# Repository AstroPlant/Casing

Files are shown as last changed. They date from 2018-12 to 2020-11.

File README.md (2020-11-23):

# Casing

## Variants
There are three casing variants:

### `original/`
All CAD and other designs for the AstroPlant original casing / enclosure / top panel.
This casing design requires a large laser cutter that can fit panels larger than 130cm in length.
The other files, developed by Swiss fablab Onlfait, are more suitable for smaller laser cutters.

### `onlfait/`
All CAD and other designs for the AstroPlant Onlfait casing / enclosure / top panel.
This casing design can be used with smaller laser cutters (900x600mm).

### `LiteEd/`
All CAD and other designs for the AstroPlant Lite Edition casing / enclosure / top panel.
This casing design is a small size versión of original Maker Edition with some other improvements,
developed by Araiva (Spain) in order to save money.

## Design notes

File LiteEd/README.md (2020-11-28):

# AstroPlant Maker LITE Edition

We have recently involved in the AstroPlant Citizen Science Project. After building our first "Maker Edition (ME)" we considered to do some changes in order to save costs of materials to build the kit. This is our first version of new design called "Maker LITE Edition (MLE)".

Main features are:

- Smaller size and low-cost version
- A power-supply unit hounsing made in plywood (avoiding 3D printed power-supply unit housing)
- A DIY hydroponic kit using IKEA 365+ containers

## Files in this folder

This folder includes files to build the Lite version of Maker Edition. You should use a 6 mm plywood/multiplex or another material with same thinkness.

- Astroplant_v5.21_6mm multiplex_MLE_Laser.dxf >>> Lasercut CAD drawings
- Astroplant_v5.21_6mm multiplex_MLE_L20x10x1.5.dxf >>> Drawings to cut L-shapes
- MLE_BOM.xlsx >>> Bill of materials including screws and components to build the hydroponic kit
- AstroPlant costs ME vs MLE.xlsx >>> Estimated cost savings vs Maker Edition

## Details, features and instructions

Follow the link and find instructions, pictures, etc... including a DIY hydroponic kit

https://astroplant.gitbook.io/ap-community-projects/astroplant-maker-lite-edition

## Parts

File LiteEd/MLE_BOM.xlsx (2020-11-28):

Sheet: Screws
SCREWS AND NUTS - DETAIL |  |  |  |  |  | SCREWS AND NUTS
 |  | Screws | Units | Nuts | Units | Screws | Units | Nuts | Units
Case | Power supply housing and display mount | M4x12 | 12 | M4 | 12 | M2x10 | 6 | M2 | 6
 | Main case | M4x20 | 21 | M4 | 21 | M2,5x12 | 7 | M2,5 | 19
 | L 20x10x1,5 (sliding door and hydroponic base) | M3x10 | 12 | M3 | 12 | M2,5x20 | 4 | M3 | 30
Component | Fans | M3x20 | 6 | M3 | 6 | M3x10 | 16 | M4 | 33
 | LED | M3x10 | 4 | M3 |  | M3x20 | 10
 | RPi | M2,5x20 | 4 | M2,5 | 12 | M4x12 | 12
 | Camera | M2x10 | 4 | M2 | 4 | M4x20 | 21
 | Extension shield | M3x20 | 4 | M3 | 12
 | Lux sensor | M2x10 | 2 | M2 | 2
 | T/H sensor | M2,5x12 | 1 | M2,5 | 1
 | Display | M2,5x12 | 2 | M2,5 | 2
 | Power supply and switch | M2,5x12 | 4 | M2,5 | 4
 |  |  | 76 |  | 88 |  | 76 |  | 88
 | You can use extra nuts in RPi and Extension Shield to lift and separate these components from the wood panel

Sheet: DIY hydroponic
DIY Hydroponic kit, BOM
Component | Shop | Price | Link
Solution container | IKEA | 3.00 € | https://www.ikea.com/es/es/p/ikea-365-recipiente-rectangular-plastico-60393066/
Plant container | IKEA | 2.00 € | https://www.ikea.com/es/es/p/ikea-365-recipiente-rectangular-plastico-60359152/
Alternative plant container | IKEA | 1.50 € | https://www.ikea.com/es/es/p/ikea-365-recipiente-rectangular-plastico-40359148/
Grave cleaner | Amazon | 11.00 € | https://www.amazon.es/Sera-08550-Aspiradora-Elimina-cuidadosamente-suciedad/dp/B0013ZAEM0?__mk_es_ES=%C3%85M%C3%85%C5%BD%C3%95%C3%91
Air compressor | AliExpress | 4.00 € | https://es.aliexpress.com/item/4000354631274.html
L-Connector 8/8 mm. | AliExpress | 0.29 € | https://es.aliexpress.com/item/32996398304.html?scm_id=1007.14976.189023.0&scm-url=1007.14976.189023.0
Y-Connector 8/8/8 mm. | AliExpress | 0.33 € | https://es.aliexpress.com/item/1005001391306435.html?spm=a2g0s.9042311.0.0.324a63c0RPETpH
PVC Hose 8/10 mm. | AliExpress | 1.37 € | https://es.aliexpress.com/item/10000312761098.html?scm_id=1007.14976.189023.0&scm-url=1007.14976.189023.0
Total price |  | 23.49 €

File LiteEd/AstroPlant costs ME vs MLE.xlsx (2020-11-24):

 |  | Costs |  | Comments
 | Item (Exc. VAT) | Maker Ed. | Maker Lite Ed.
1.1 | AstroPlant kit | 400 € | 400 € | Prices for AstroPlant electrocnic kit may suffer changes, please check it
1.2 | AstroPlant kit shipping | 40 € | 40 € | To Spain
1.3 | L20x20x1,5 | 10 € | 10 €
1.4 | Laser | 117 € | 54 €
1.5 | 3D Power supply casing | 75 € |  | In MLE casing is made in plywood and laser costs included in 1.4 (I do now own a 3D Printer and I have to buy it)
1.6 | Waterfarm | 65 € |  | Include air pump
1.7 | IKEA Containers |  | 5 € | To make DIY hydroponic kit
1.8 | Air pump |  | 10 € | To make DIY hydroponic kit
1.9 | DIY Hydroponics accessories |  | 5 € | Like "T" connectors, etc... (you can find them by Aliexpress or Amazon)
 | Total | 707 € | 504 €
 | VAT (21%) | 148.47 € | 105.84 €
 | Total | 855.47 € | 609.84 €
 | Total saved cost (Incl. VAT): |  | -245.63 €

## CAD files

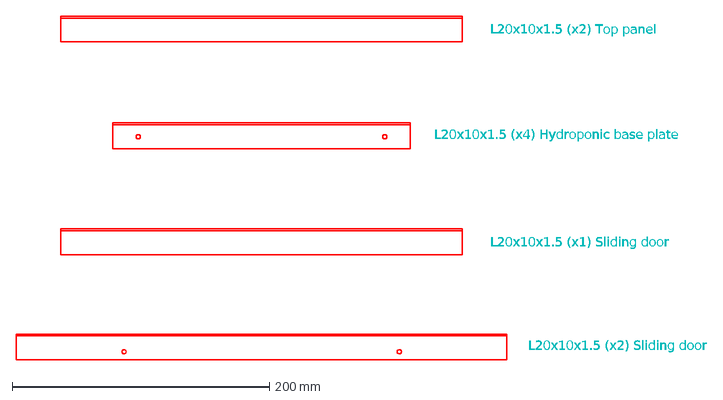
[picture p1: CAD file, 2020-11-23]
LiteEd/Astroplant_v5.21_6mm multiplex_MLE_L20x10x1.5.dxf
L20x10x1.5 (x2) Top panel
L20x10x1.5 (x4) Hydroponic base plate
L20x10x1.5 (x1) Sliding door
L20x10x1.5 (x2) Sliding door

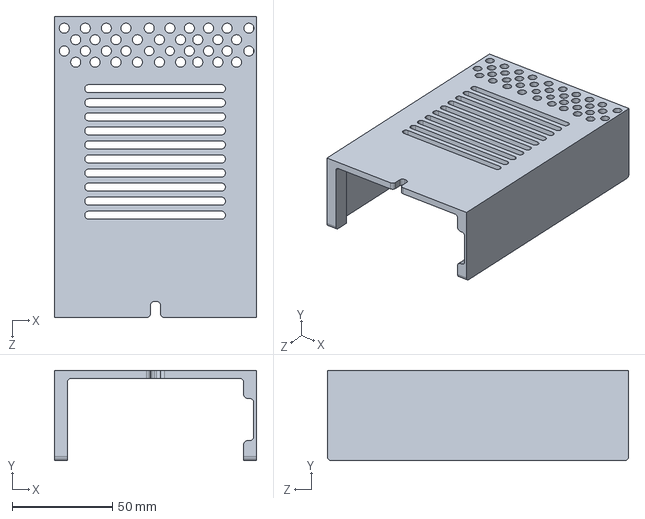
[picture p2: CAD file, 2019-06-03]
onlfait/v2.0/casingpowersupply.step
100.6 x 45.0 x 150.0 mm

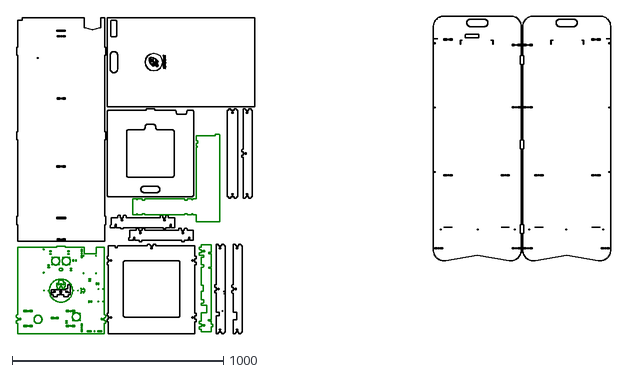
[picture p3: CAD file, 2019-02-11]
original/Laserfiles_v5.21_6mm multiplex.dxf
2812.3 x 1504.4

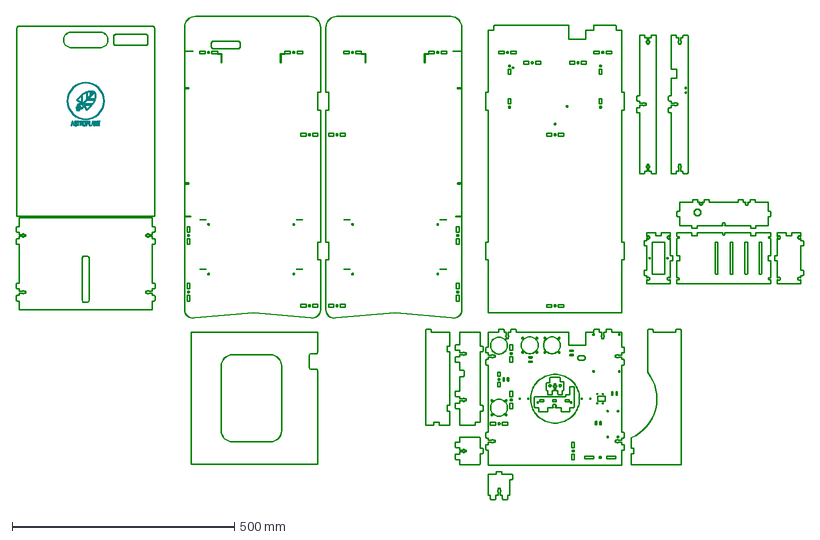
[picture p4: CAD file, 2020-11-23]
LiteEd/Astroplant_v5.21_6mm multiplex_MLE_Laser.dxf
1771.6 x 1087.4 mm

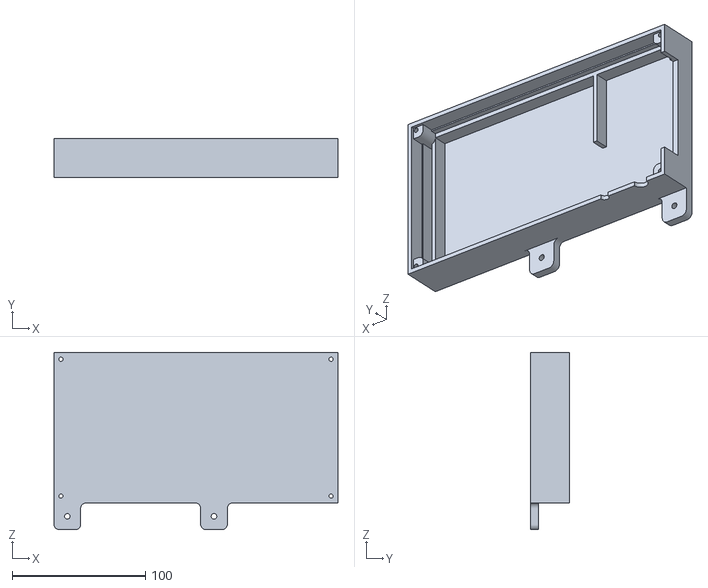
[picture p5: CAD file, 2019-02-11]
original/v5.21-Housing_powerconverter_rev02-Boss-Extrude1.STL
213.0 x 29.0 x 133.0

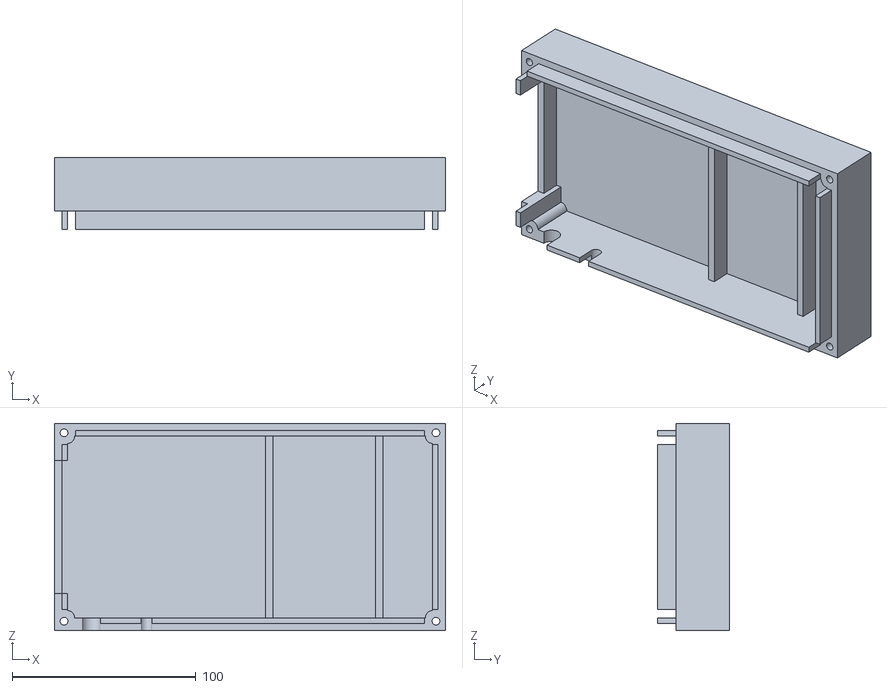
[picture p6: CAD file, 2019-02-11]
original/v5.21-Housing_powerconverter_rev02-Mirror1.STL
213.0 x 39.0 x 113.0

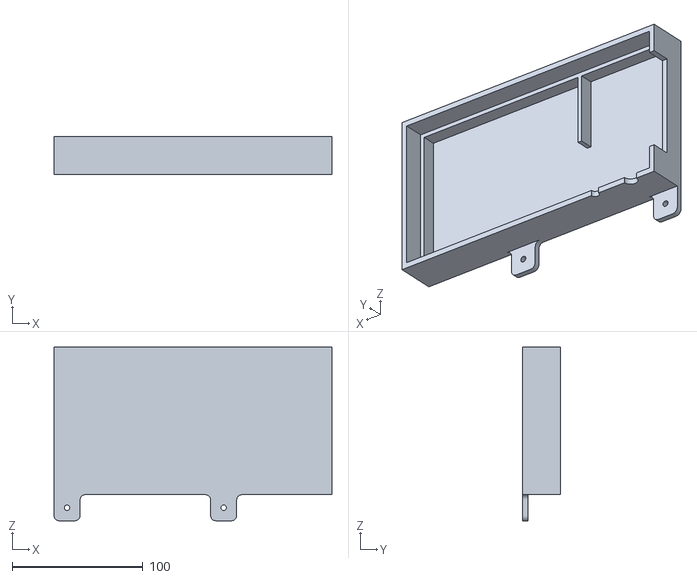
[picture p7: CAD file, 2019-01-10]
original/Bottom_Housing_powerconverter_v5.1_R2.STL
213.0 x 29.0 x 133.0

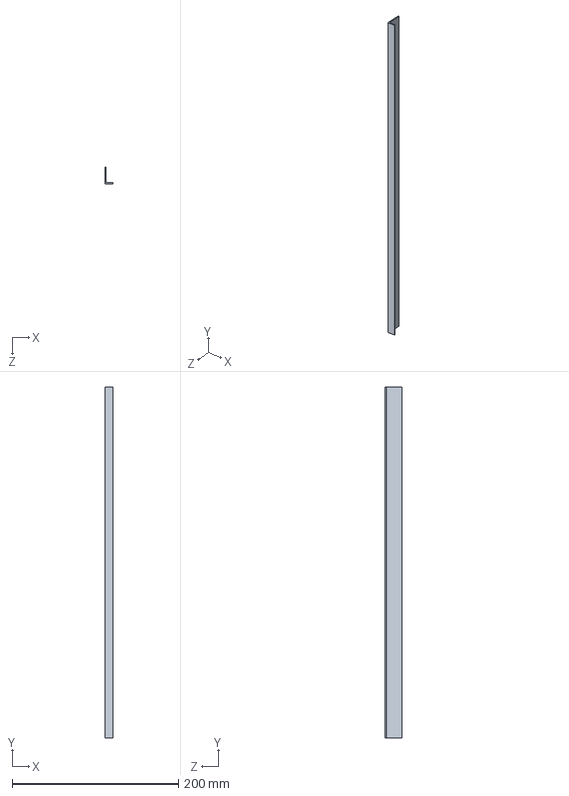
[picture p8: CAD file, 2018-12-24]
original/L Profile_support_basisplate_422x20x10_2x_v5.1.STEP
10.0 x 422.0 x 20.0 mm

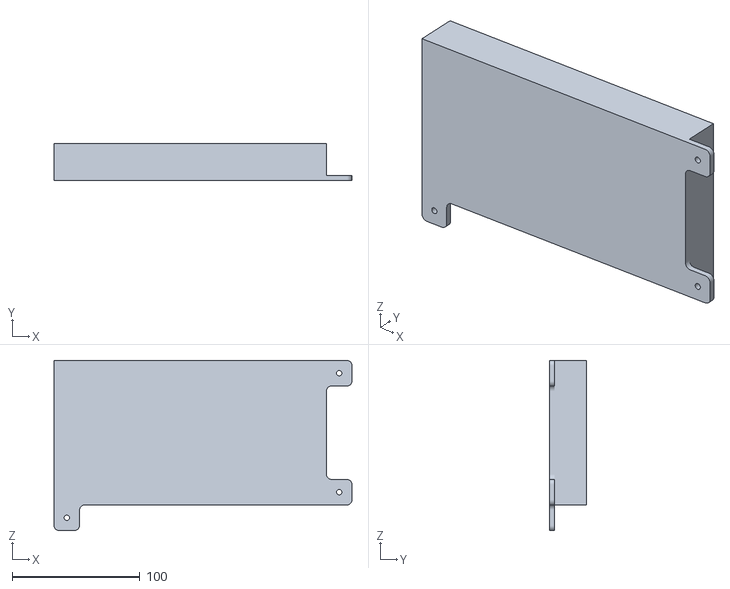
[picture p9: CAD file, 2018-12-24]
original/Housing_powerconverter_BOTTOM_v5.1.STL
233.0 x 29.0 x 133.0

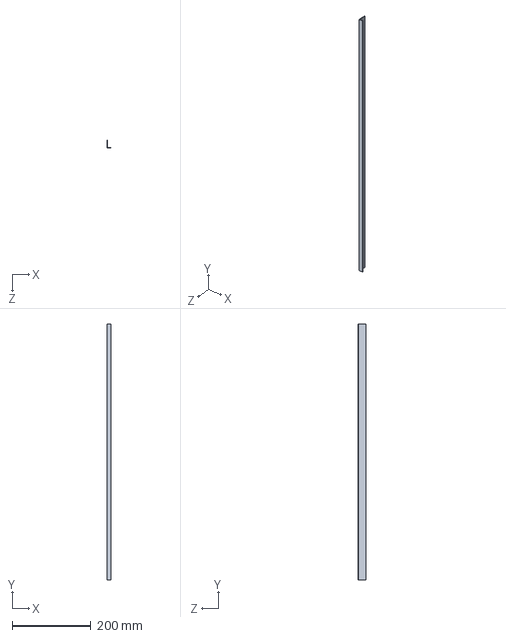
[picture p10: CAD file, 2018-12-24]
original/L Profile_frontpanel_650x20x10_2x_v5.1.STEP
10.0 x 650.0 x 20.0 mm

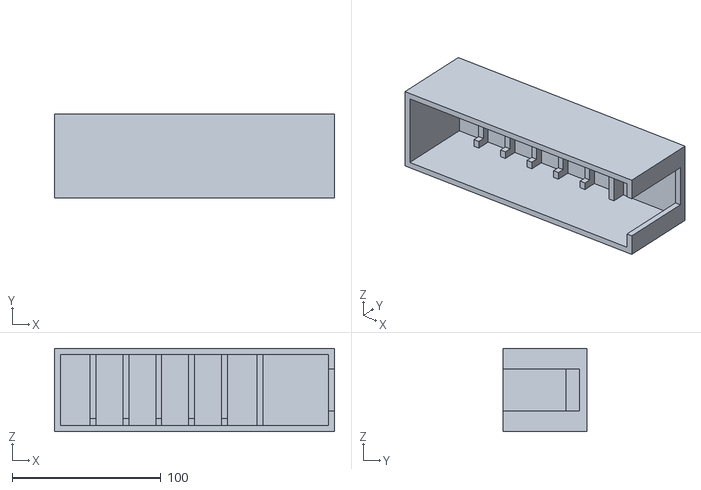
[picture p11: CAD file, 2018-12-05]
original/3D printing FDM_Housing_powerconverter_toppart.STL
188.0 x 56.5 x 56.0

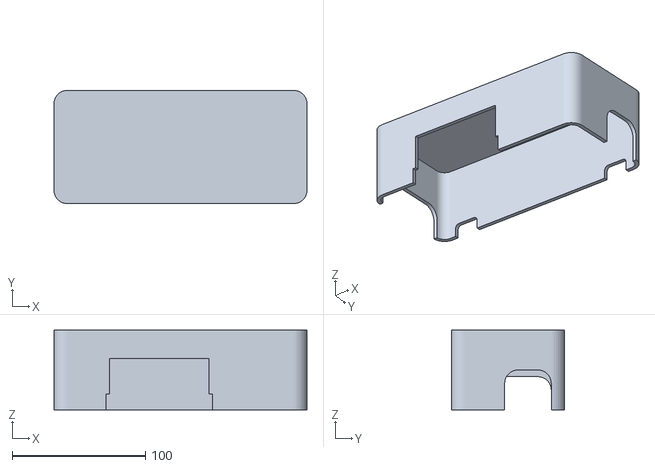
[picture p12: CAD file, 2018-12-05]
original/3D printing FDM_Housing board.STL
190.0 x 85.0 x 60.0

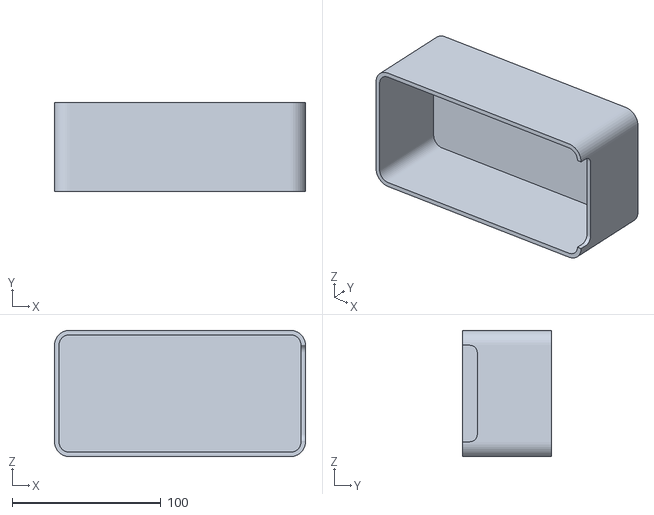
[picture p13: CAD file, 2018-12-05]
original/3D printing FDM_Housing sensors.STL
169.0 x 60.0 x 85.0

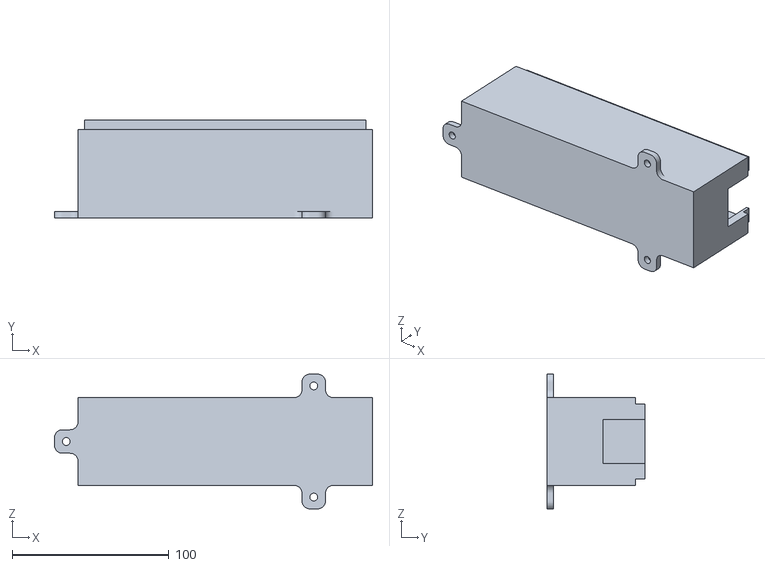
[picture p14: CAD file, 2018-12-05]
original/3D printing FDM_Housing_powerconverter_bottompart.STL
203.0 x 62.5 x 86.0

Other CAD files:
original/Top_Housing_powerconverter_v5.1_R2.STL
original/Housing_powerconverter_TOP_v5.1.STL
onlfait/v1.8/planche_11.dxf
onlfait/v1.8/planche_10.dxf
onlfait/v1.8/planche_1.dxf
onlfait/v1.8/planche_12.dxf
onlfait/v1.8/planche_2.dxf
onlfait/v1.8/planche_3.dxf
onlfait/v1.8/planche_4.dxf
onlfait/v1.8/planche_5.dxf
onlfait/v1.8/planche_6.dxf
onlfait/v1.8/planche_7.dxf
onlfait/v1.8/planche_8.dxf
onlfait/v1.8/planche_9.dxf
onlfait/v2.0/CasingPowersupply.stl
onlfait/v2.0/casingpowersupply.igs
onlfait/v2.0/casingpowersupply.sldprt

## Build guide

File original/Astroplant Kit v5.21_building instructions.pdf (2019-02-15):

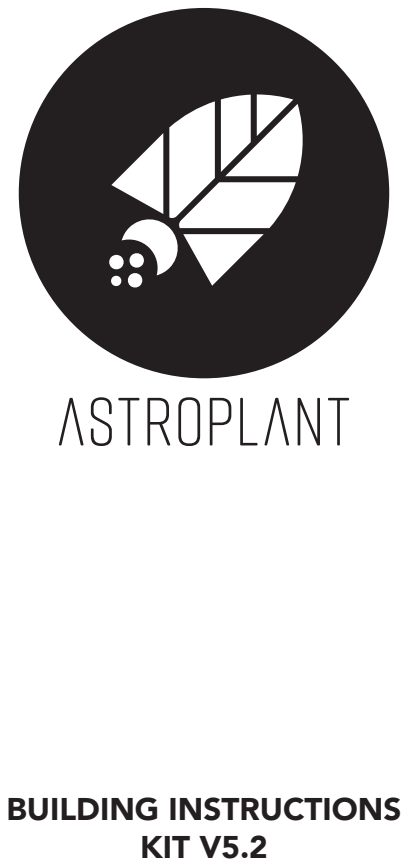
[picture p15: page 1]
BUILDING INSTRUCTIONS KIT V5.2

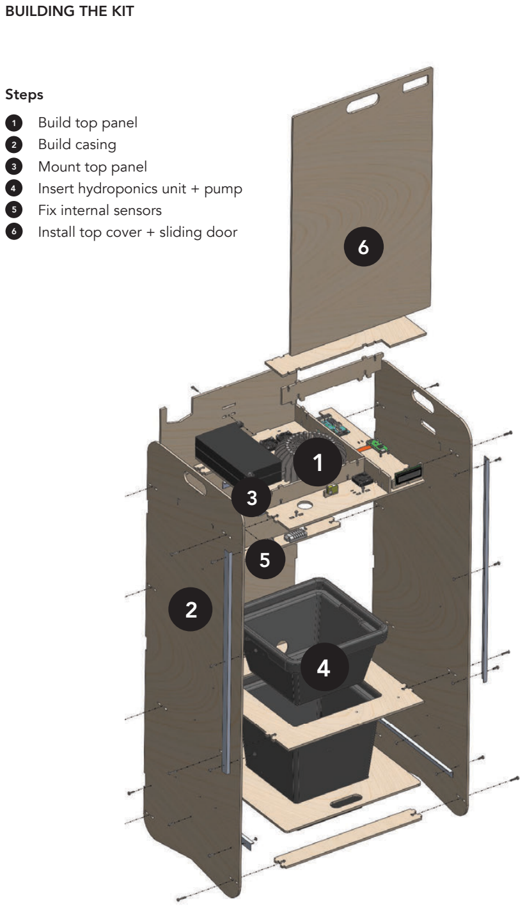
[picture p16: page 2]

1
2
3
4
5
6

BUILDING THE KIT

1

2

3

5

4

6

Steps

Build top panel
Build casing
Mount top panel
Insert hydroponics unit + pump Fix internal sensors
Install top cover + sliding door

PART LIST

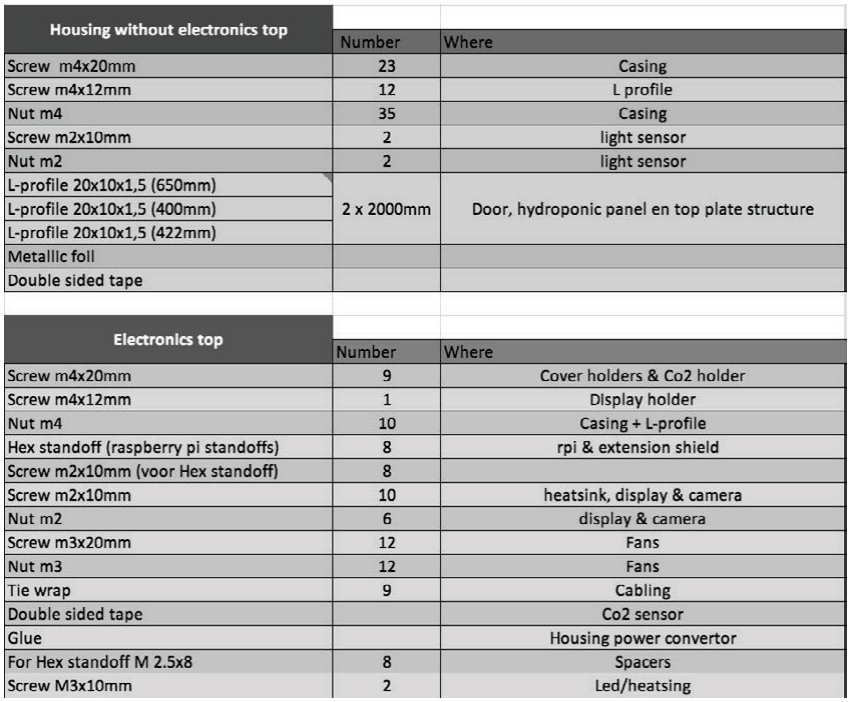
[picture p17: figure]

1

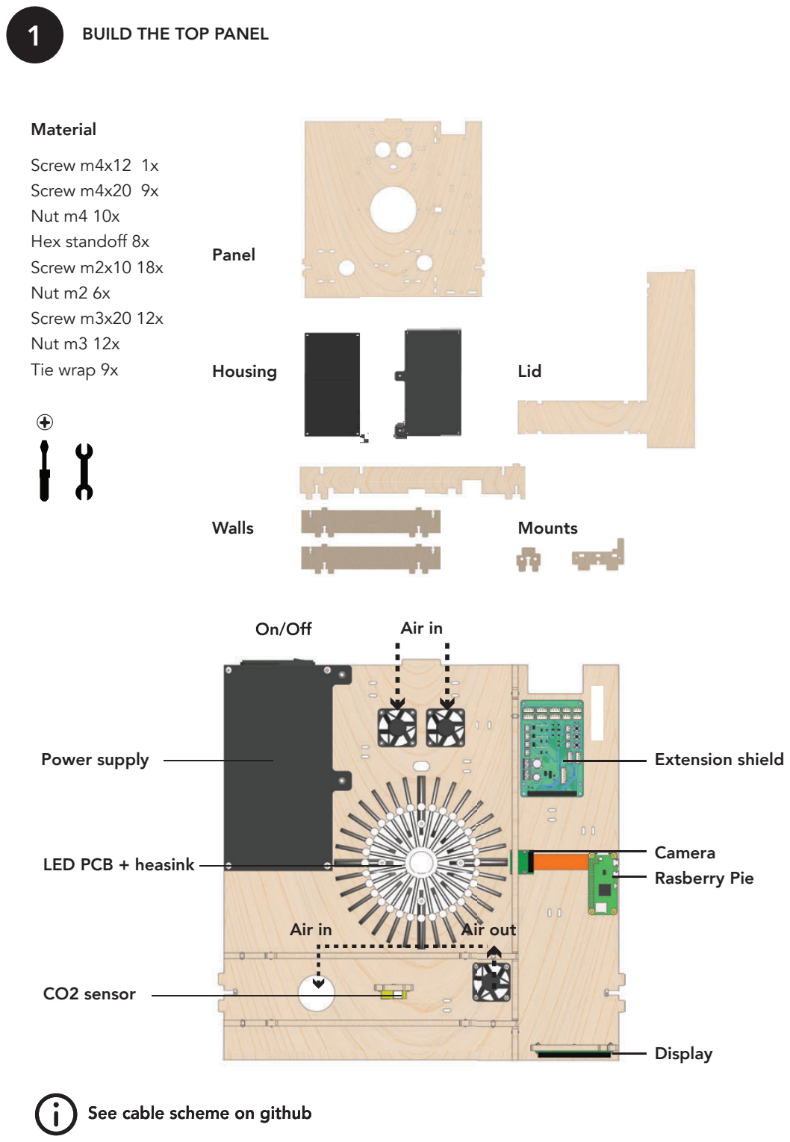
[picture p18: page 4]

On/Off

Material

Screw m4x12 1x
Screw m4x20 9x
Nut m4 10x
Hex standoff 8x
Screw m2x10 18x
Nut m2 6x
Screw m3x20 12x
Nut m3 12x
Tie wrap 9x

Walls

Housing | Lid

Mounts

Panel

BUILD THE TOP PANEL

See cable scheme on github

On/Off

Air in | Air out

Air in

Power supply | Extension shield

Rasberry Pie

Display

Camera LED PCB + heasink

CO2 sensor

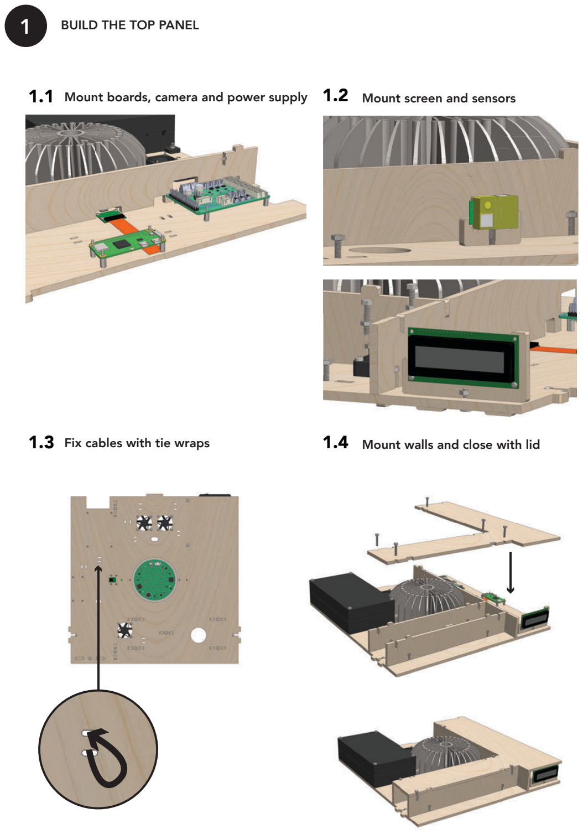
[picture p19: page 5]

Tie wrap

1.3 Fix cables with tie wraps | 1.4 Mount walls and close with lid

### 1.1 Mount boards, camera and power supply 1.2 Mount screen and sensors

Tie wrap

### 1 BUILD THE TOP PANEL

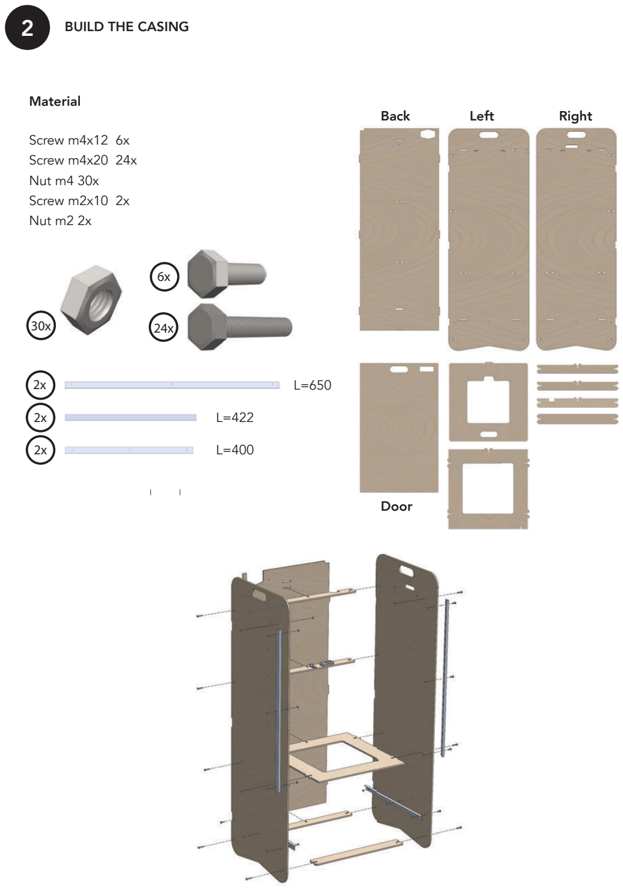
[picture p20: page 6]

Back | Left | Right
30x | 24x 6x

Material

Screw m4x12 6x
Screw m4x20 24x
Nut m4 30x
Screw m2x10 2x
Nut m2 2x

2x

2x

2x

L=650

Door

L=422

L=400

### 2 BUILD THE CASING

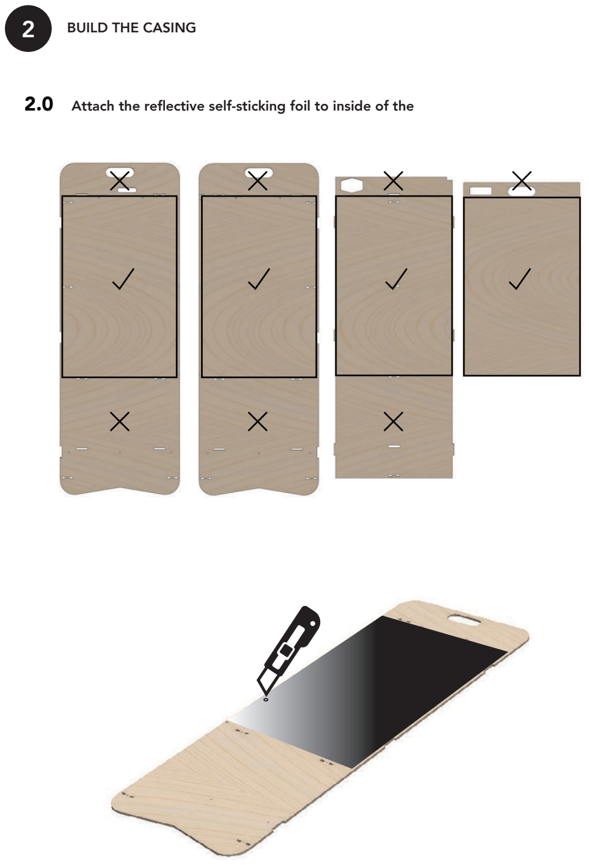
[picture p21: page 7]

### 2 BUILD THE CASING

### 2.0 Attach the reflective self-sticking foil to inside of the

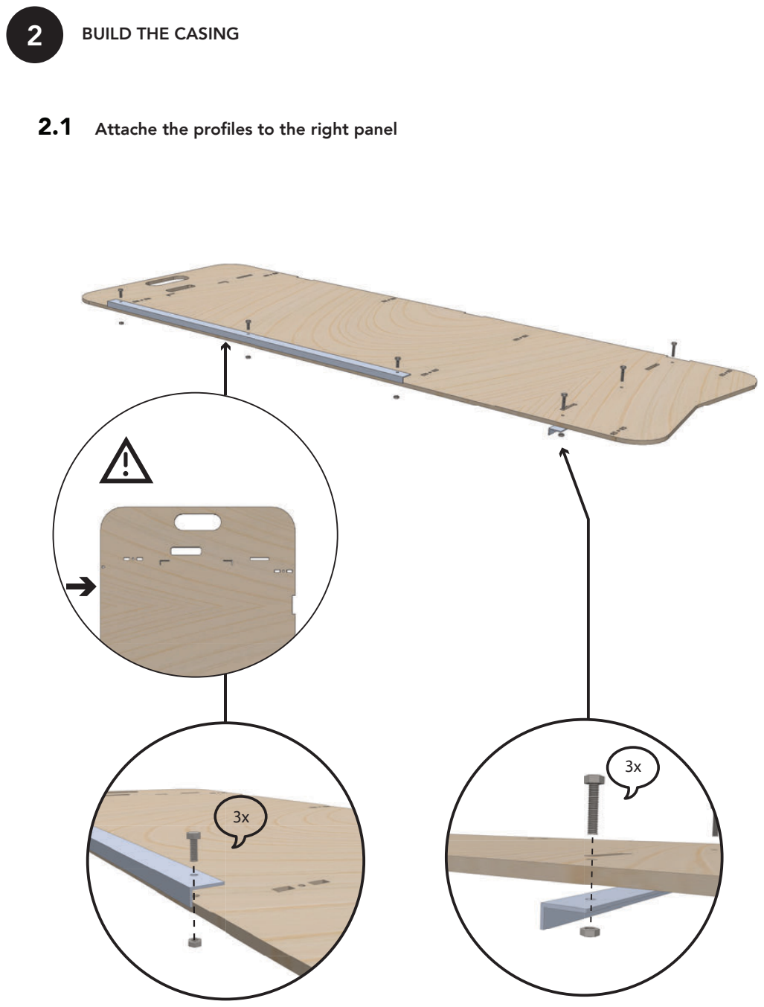
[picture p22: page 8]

3x

3x

### 2.1 Attache the profiles to the right panel

### 2 BUILD THE CASING

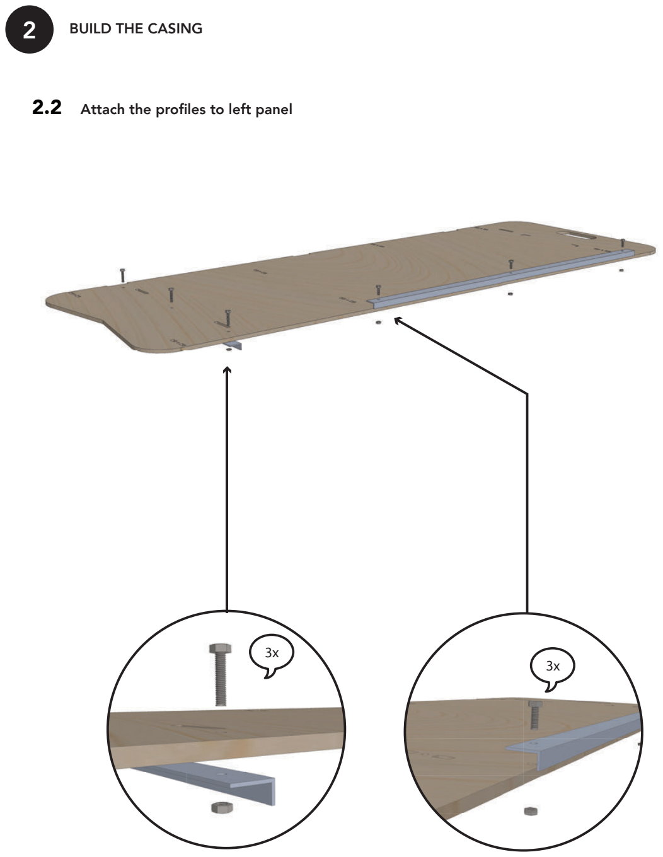
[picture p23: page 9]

3x
3x

### 2 BUILD THE CASING

### 2.2 Attach the profiles to left panel

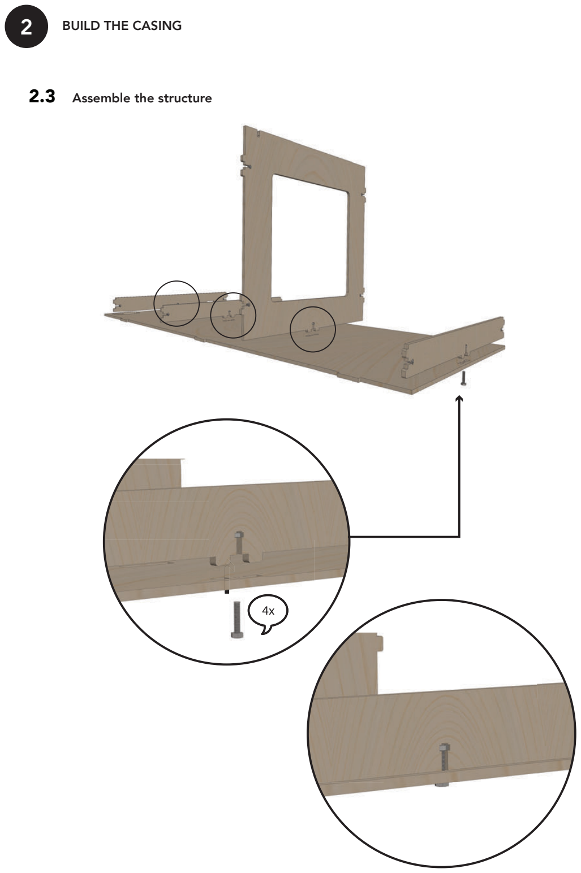
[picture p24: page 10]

### 2 BUILD THE CASING

### 2.3 Assemble the structure

4x

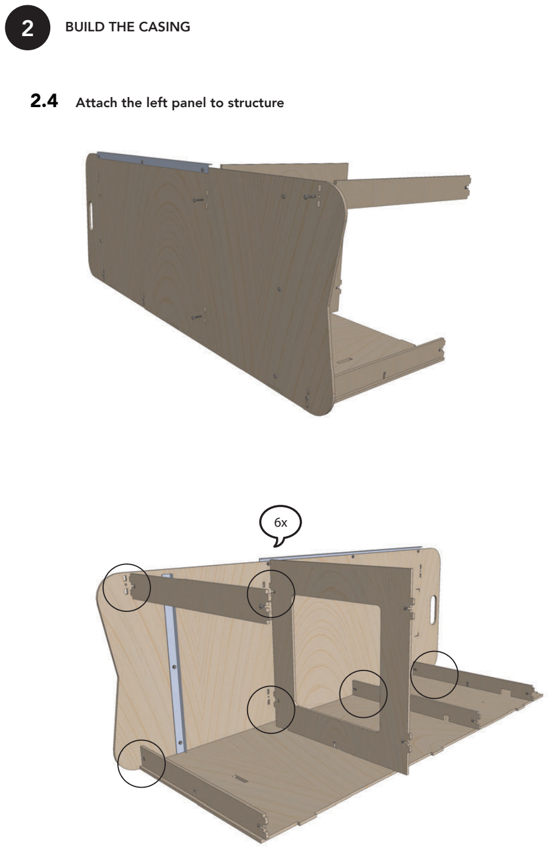
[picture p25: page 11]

### 2 BUILD THE CASING

6x

### 2.4 Attach the left panel to structure

2

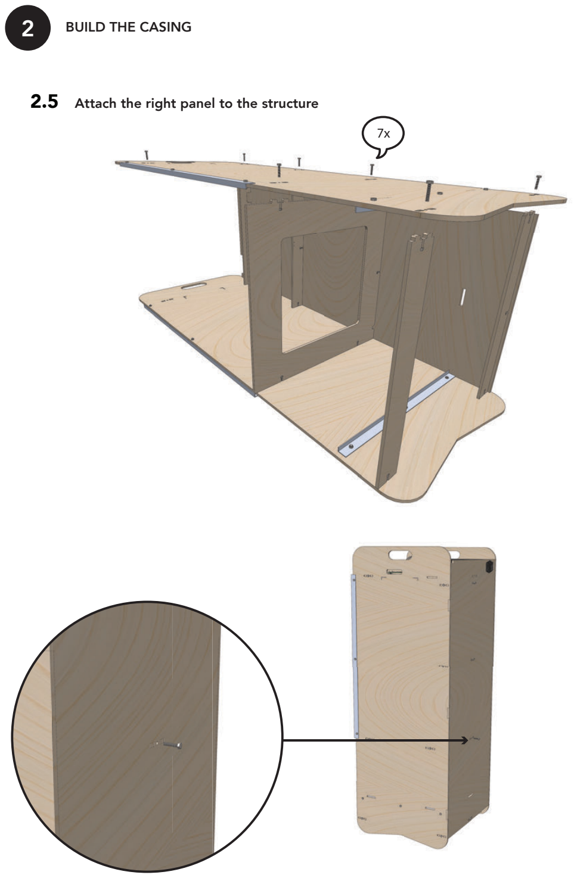
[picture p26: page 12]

BUILD THE CASING

### 2.5 Attach the right panel to the structure

7x

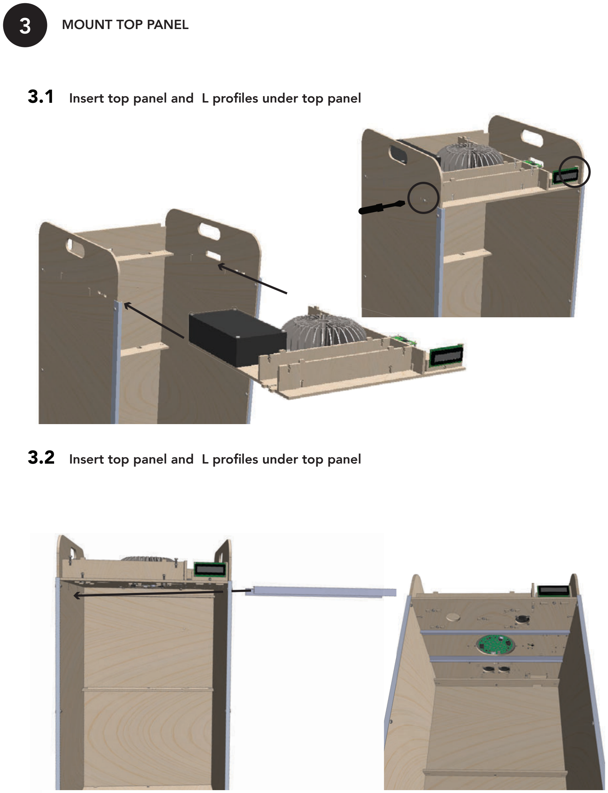
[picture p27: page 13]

### 3 MOUNT TOP PANEL

### 3.1 Insert top panel and L profiles under top panel

### 3.2 Insert top panel and L profiles under top panel

4

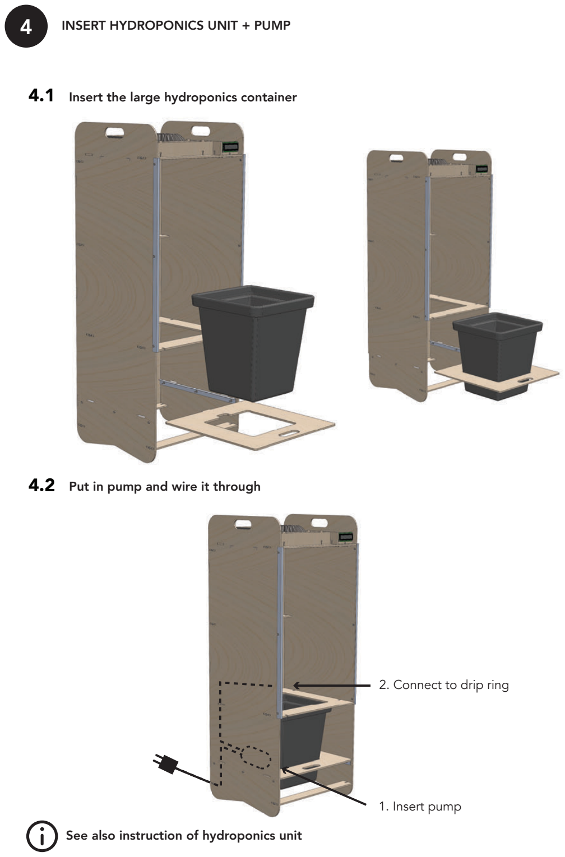
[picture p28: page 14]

INSERT HYDROPONICS UNIT + PUMP

### 4.1 Insert the large hydroponics container

### 4.2 Put in pump and wire it through

2. Connect to drip ring
1. Insert pump
See also instruction of hydroponics unit

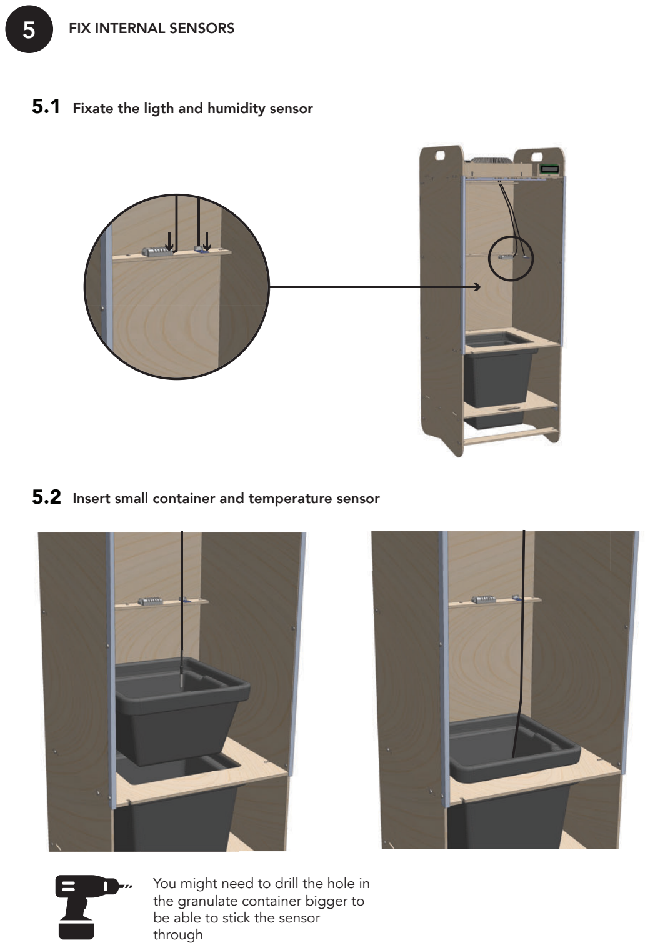
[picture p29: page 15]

You might need to drill the hole in the granulate container bigger to be able to stick the sensor through

### 5 FIX INTERNAL SENSORS

### 5.1 Fixate the ligth and humidity sensor

### 5.2 Insert small container and temperature sensor

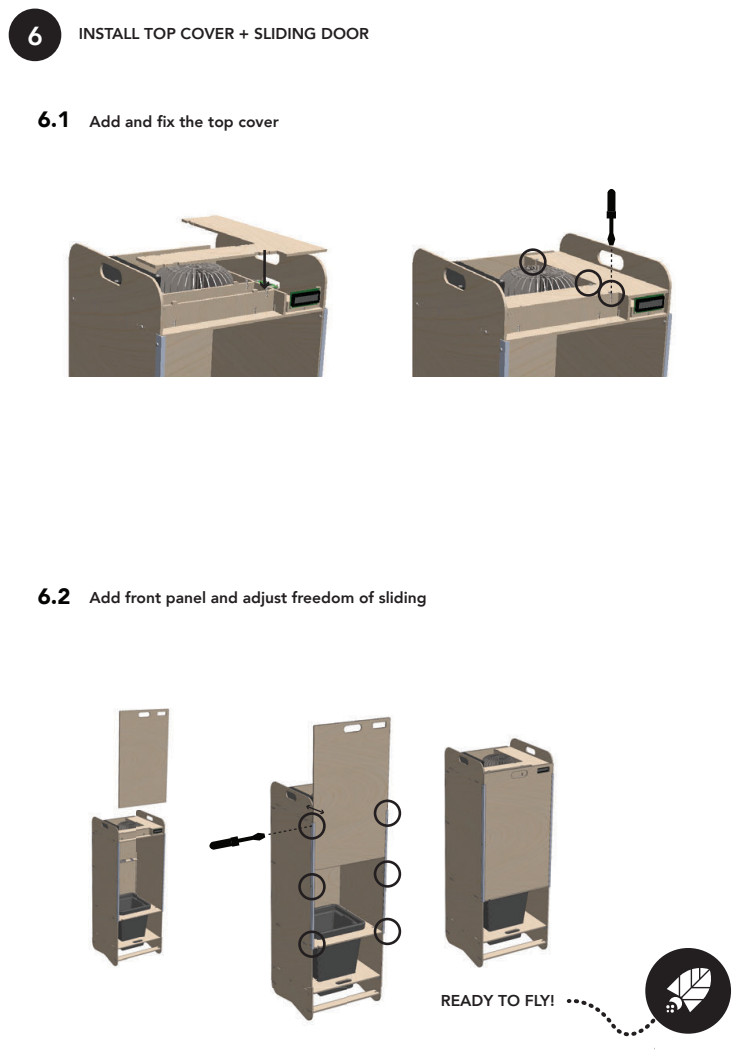
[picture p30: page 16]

6 INSTALL TOP COVER + SLIDING DOOR

6.1 Add and fix the top cover

6.2 Add front panel and adjust freedom of sliding

READY TO FLY!

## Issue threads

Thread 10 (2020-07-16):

### ISSUE TITLE
Electronics instructions could use more pictures

### ISSUE THREAD

**Issue by jklingen92** [AstroPlant/Casing#10]
I'm attempting to build the electronics panel and I made a mistake that will set me back some amount of time. I connected the ferrule tipped power supply wires into the power supply and they wouldn't come out. While trying to remove them, I instead remove the connector from the panel. I think with more pictures of the wires and the connectors they are going to, I might not have made this mistake.

![IMG_20200627_191551~2](https://user-images.githubusercontent.com/8923518/85934020-7203ee00-b8ab-11ea-9048-b3492b03a772.jpg)
![IMG_20200627_191636](https://user-images.githubusercontent.com/8923518/85934021-729c8480-b8ab-11ea-946f-2896945e6a93.jpg)
![IMG_20200627_191653](https://user-images.githubusercontent.com/8923518/85934022-73cdb180-b8ab-11ea-878b-ca241bccbf39.jpg)

Does anyone have any recommendations for how I can solve this? I may be able to access an electronic shop but I'm not sure.

**Comment by SidneyNiccolson** [comment]
Hi Jake,

Very unfortunate to hear that the connector came loose. 

The connector is a: wago 2060 402 [more info](https://www.tme.eu/en/details/2060-402_0998-404/led-connectors/wago/2060-402-998-404/). I'm not an electronics expert, but you could either 1) try to remove the cable or if that doesn't work 2) order the component from an electronics shop. You might have to look at larger suppliers like TME, DigiKey or Mouser. 
Once you managed the above, you'll need to re-solder the component back on the board. Officially this is done with "reflow soldering". 

For the Wago component, the only wires that fit are the bare-metal ones. Do you have access to gitbook? If not, I still have access I believe and could add a picture there next to the remark. 

I hope this helps!

**Comment by jklingen92** [comment]
I haven't used gitbook before so I'm not sure if I can edit or not.

**Comment by thiemehennis** [comment]
please share the emailaddress you want to use for Gitbook here so I can add
you as a writer.


--
Thieme Hennis PhD // +31651855220 // Amsterdam, Den Haag

**Comment by jklingen92** [comment]
jklingen92@gmail.com

**Comment by SidneyNiccolson** [comment]
@jklingen92 
I was wondering how to progress with fixing the broken part went? Additionally do you have access now? 

I updated the gitbook with a simple picture to let people now which cables to use. Feel free to update it with nicer pictures or texts.

**Comment by SidneyNiccolson** [comment]
Hi @jklingen92 ,

I'm closing this issue now as it is stale. If you want to re-open it, please ask it on Slack "Questions" channel and I'll re-open if necessary.

**Comment by jklingen92** [comment]
@SidneyNiccolson I was out of town, but I am resuming construction now. 

I do have access, and I was able to resolder the part. I haven't tested the connection, it was a tricky soldering job for a beginner, but I think that I got it on acceptably. The image on GitBook looks perfect. Thanks for that!

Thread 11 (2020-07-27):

### ISSUE TITLE
Not sure where +V1 5V from power supply should be connected

### ISSUE THREAD

**Issue by jklingen92** [AstroPlant/Casing#11]
The electronics assembly instructions don't seem to specify where the +V1 5V should be connected.Based on the wiring image and logic, I think should be connected to the extension board (although in the image, it is wiring along a different path from the 24V power cables for no obvious reason). If I'm missing some part of the instructions, please direct me, but I've looked over everything under the power supply heading (and searched the whole document - `+V1 only appears in the testing section).

**Comment by SidneyNiccolson** [comment]
@jklingen92 it is correct that the explanation was missing. I checked the other guide on "Electronics assembly from scratch" and that did contain the documentation. I think I forgot to add it in the "maker edition" guide (it is now added though). 

To answer your question, yes the +V1 should go to 5V on the extension board.  If you are going to power the RPi through the AC/DC converter make sure your jumper configuration is correct on the extension board. 

All the best, 

Sidney

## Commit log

2018-12-05 Add files via upload
    Maker files Astroplant V5
    [3D printing FDM_Housing board.STL, 3D printing FDM_Housing sensors.STL, 3D printing FDM_Housing_powerconverter_bottompart.STL, 3D printing FDM_Housing_powercon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]
2018-12-11 made note about current improvements
2018-12-24 Add files via upload
    These are the maker files for Astroplant v5.1 with an improved construction and a smaller number of parts.
    Merry Christmas!
    [Housing_powerconverter_BOTTOM_v5.1.STL, Housing_powerconverter_TOP_v5.1.STL, L Profile_frontpanel_650x20x10_2x_v5.1.STEP, L Profile_support_basisplate_422x20x1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]
2019-01-10 New top panel layout
    New position of fans due to restricted cable length.
2019-01-10 New converter housing 3d print FDM
    different orientation fitting new top panel
    [Bottom_Housing_powerconverter_v5.1_R2.STL, Top_Housing_powerconverter_v5.1_R2.STL]
2019-02-11 Add files via upload
    Latest maker files v5.21
    STLs made for 3Dprinting on FDM printers (Ultimaker or other)
    [Laserfiles_v5.21_6mm multiplex.dxf, v5.21-Housing_powerconverter_rev02-Boss-Extrude1.STL, v5.21-Housing_powerconverter_rev02-Mirror1.STL]
2019-05-06 Move the distinct versions to separate subdirectories.
    Update README to match.
    [3D printing FDM_Housing board.STL, 3D printing FDM_Housing sensors.STL, 3D printing FDM_Housing_powerconverter_bottompart.STL, 3D printing FDM_Housing_powercon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]
2019-05-20 Add files via upload
    Updated Onl'Fait casing drawings
    [board_1.dxf, board_10.dxf, board_11.dxf, board_12.dxf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]
2019-05-20 Move Onlfait files.
    [board_1.dxf, board_10.dxf, board_11.dxf, board_12.dxf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]
2019-06-03 Move power-supply files to v2.0 directory.
    [CasingPowersupply.stl, board_1.dxf, board_10.dxf, board_11.dxf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]
2020-11-22 Rename Astroplant_v5.21_6mm multiplex_MLE_Laser.dxf to LiteEd/Astroplant_v5.21_6mm multiplex_MLE_Laser.dxf
    [Astroplant_v5.21_6mm multiplex_MLE_Laser.dxf]
